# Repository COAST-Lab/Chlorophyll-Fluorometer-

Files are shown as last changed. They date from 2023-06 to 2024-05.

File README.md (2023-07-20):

# Low-Cost Chlorophyll Fluorometer 

This GitHub repository is intendied to serve as information and a guide to a low-cost chlorophyll flourometer. This fluorometer is based off of, *In situ Measurements of Phytoplankton Fluorescence Using Low Cost Electronics* and *Hardware Selection and Performance of Low-Cost Fluorometers* which can be found at https://doi.org/10.3390/s130607872 and https://doi.org/10.3390/s22062319 respectively.

## The Basics
This project is composed of a sensor packaged designed to induuce chlorphyll fluorescence and convert these values into readable measurments. This sensor contains a Particle Argon Microcontroller set to 2.30 firmware, an Arduino-Based Addalogger RTC with an SD card for data reading and writting, a TSL 2591 light sensor, an AW9523 GPIO Expander and LED Driver Guide and a Blue LED 430L for chlorophyll excitation. This design uses I2C comunication. 

# Sesnsor Construction and Testing 

## Assembly

### Step 1:
Stack the Argon Microcontroller on top of the RTC Addalogger. Connect the Argon Microcontroller to the 3.3V power source and Ground. 
### Step 2:
Set up I2C communication between the Argon Particle with the TSL 2591 and AW9523. Connect the SCL and SDA pins from the TSL 2591 Light Sensor and AW9523 GPIO Expander to the SCL and SDA pins on the Argon Microncontroller. Connect the TSL 2591 VIN pin to the 3.3V and GND pin to Ground. Connect the AW9523 VIN Pin to the 3.3V and the GND pin to Ground.
### Step 3:
Set up the LED with the AW9523. NOTE: LED negative side is connected to the pin and the positive to the power. The LED will connect to the 0 pin on the AW9523. 
### Step 4:
Assemnple the housing. The housing will position the LED and the AW9523 at a 90 degree angle as well as will be an opage design as to eliminate any ambient light from impacting the measurements. This design will then be enclosed in a waterproof box. Design materials and models can be found at https://github.com/COAST-Lab/Chlorophyll-Fluorometer-/tree/main/Firmware 
### Step 5:
Callibrate the Sensor to convert Lux values to readable measurements, based off of commerical fluoromter values. 
## Step 6:
Begin water testing 

# LED Testing 
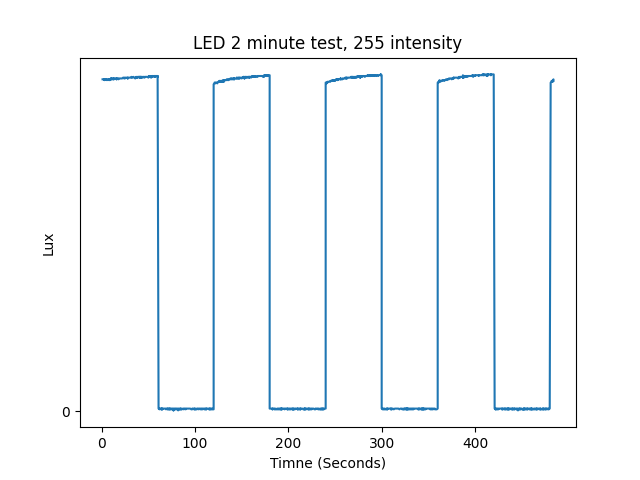
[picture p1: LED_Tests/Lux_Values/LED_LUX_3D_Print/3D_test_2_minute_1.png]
After the fluorometer was constructed, tests were run where the LED was directly facing the light sensor in a dark enviornment. This test involved turning on the LED for 2 minutes and then off for 2 minutes for 5 rounds taking light measurements throughout.  It was found that the LED was havign a steady increase in current casuing the light sensor to have an increase in values.  

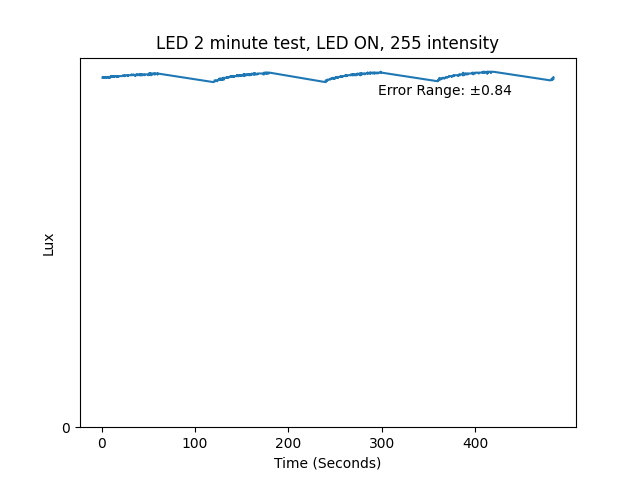
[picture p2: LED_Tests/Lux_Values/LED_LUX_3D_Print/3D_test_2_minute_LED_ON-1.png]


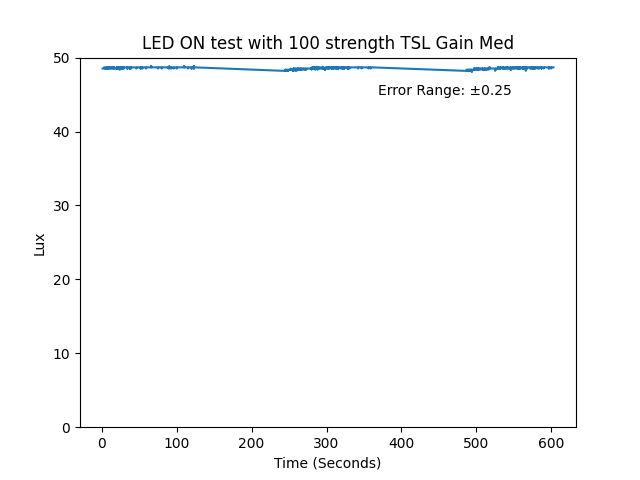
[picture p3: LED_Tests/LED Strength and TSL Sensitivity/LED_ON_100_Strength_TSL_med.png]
After many trials of this the intensity of of the LED light was changed as well as the light sensor gain (sensitivity) value. The LED can be set to any intensity from 0-255 via the AW9523. The light sesnor can be set to a gain of low, med, high and max. The LED was found to have the least variability when set to an intensity of 100 and a when the light sensor was set to a gain of med. 

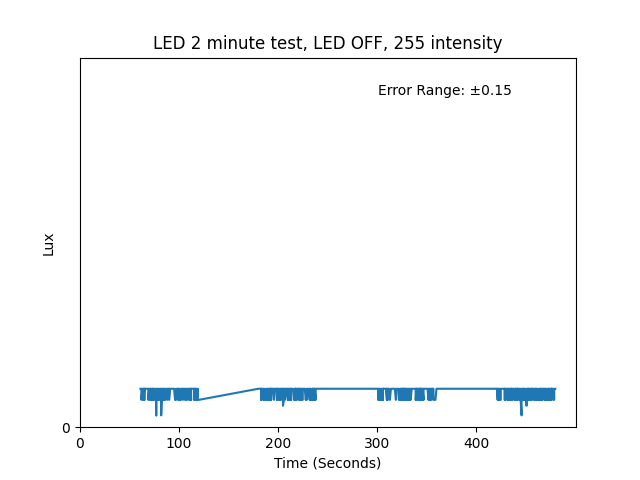
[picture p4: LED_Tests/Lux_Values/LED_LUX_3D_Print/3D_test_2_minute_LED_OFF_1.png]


After many trials of this the intensity of of the LED light was changed as well as the light sensor gain (sensitivity) value. The LED can be set to any intensity from 0-255 via the AW9523. The light sesnor can be set to a gain of low, med, high and max. The LED was found to have the least variability when set to an intensity of 100 and a when the light sensor was set to a gain of med. 

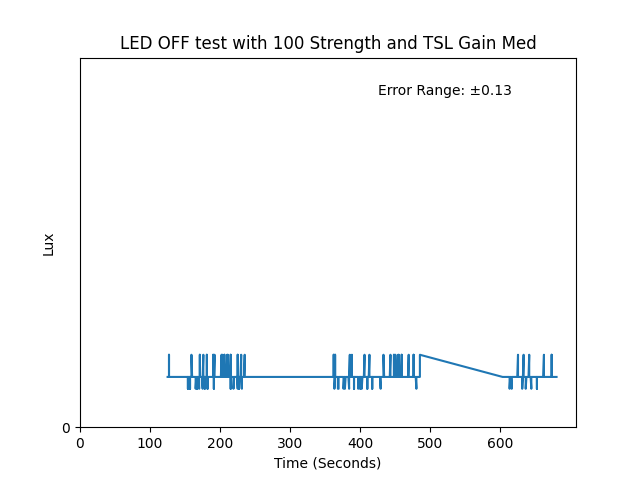
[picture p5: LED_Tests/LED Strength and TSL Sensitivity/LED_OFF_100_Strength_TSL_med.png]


```python

```

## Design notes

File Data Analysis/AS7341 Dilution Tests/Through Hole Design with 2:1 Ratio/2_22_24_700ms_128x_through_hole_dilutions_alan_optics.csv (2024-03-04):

Date and Time | ASTEP | ATIME | GAIN | LED Status | LED Intensity | Test | Seconds | Milliseconds | Type | F1 (Basic) | F2 (Basic) | F3 (Basic) | F4 (Basic) | F5 (Basic) | F6 (Basic) | F7 (Basic) | F8 (Basic) | Clear (Basic) | NIR (Basic) | Type | F1 (Raw) | F2 (Raw) | F3 (Raw) | F4 (Raw) | F5 (Raw) | F6 (Raw) | F7 (Raw) | F8 (Raw) | Clear (Raw) | NIR (Raw)
Date and Time | ASTEP | ATIME | GAIN | LED Status | LED Intensity | Test | Seconds | Milliseconds | Type | F1 (Basic) | F2 (Basic) | F3 (Basic) | F4 (Basic) | F5 (Basic) | F6 (Basic) | F7 (Basic) | F8 (Basic) | Clear (Basic) | NIR (Basic) | Type | F1 (Raw) | F2 (Raw) | F3 (Raw) | F4 (Raw) | F5 (Raw) | F6 (Raw) | F7 (Raw) | F8 (Raw) | Clear (Raw) | NIR (Raw)
2032/5/32 (Tuesday) 30:46:15 | 999 | 255 | 8 | LED ON | 255 | 0.0 | 3 | 3323 | BASIC COUNTS | 0.00 | 0.00 | 0.00 | 0.00 | 0.00 | 0.00 | 0.00 | 0.00 | 0.00 | 0.00 | RAW VALUES | 0 | 0 | 0 | 0 | 0 | 0 | 0 | 0 | 0 | 0
2032/5/32 (Tuesday) 30:46:18 | 999 | 255 | 8 | LED ON | 255 | 0.0 | 6 | 6351 | BASIC COUNTS | 0.00 | 0.01 | 0.00 | 0.00 | 0.00 | 0.00 | 0.00 | 0.00 | 0.01 | 0.00 | RAW VALUES | 398 | 637 | 57 | 29 | 20 | 23 | 29 | 18 | 620 | 0
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

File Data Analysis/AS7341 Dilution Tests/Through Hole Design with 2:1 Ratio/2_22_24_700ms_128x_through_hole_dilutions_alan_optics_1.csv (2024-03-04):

Date and Time | ASTEP | ATIME | GAIN | LED Status | LED Intensity | Test | Seconds | Milliseconds | Type | F1 (Basic) | F2 (Basic) | F3 (Basic) | F4 (Basic) | F5 (Basic) | F6 (Basic) | F7 (Basic) | F8 (Basic) | Clear (Basic) | NIR (Basic) | Type | F1 (Raw) | F2 (Raw) | F3 (Raw) | F4 (Raw) | F5 (Raw) | F6 (Raw) | F7 (Raw) | F8 (Raw) | Clear (Raw) | NIR (Raw)
2112/5/32 (Thursday) 30:46:21 | 999 | 255 | 8 | LED ON | 255 | 0.0 | 3 | 3356 | BASIC COUNTS | 0.00 | 0.00 | 0.00 | 0.00 | 0.00 | 0.00 | 0.00 | 0.00 | 0.00 | 0.00 | RAW VALUES | 0 | 0 | 0 | 0 | 0 | 0 | 0 | 0 | 0 | 0
2112/5/32 (Thursday) 30:46:24 | 999 | 255 | 8 | LED ON | 255 | 0.0 | 6 | 6383 | BASIC COUNTS | 0.00 | 0.01 | 0.00 | 0.00 | 0.00 | 0.00 | 0.00 | 0.00 | 0.01 | 0.00 | RAW VALUES | 368 | 576 | 51 | 26 | 18 | 21 | 26 | 17 | 571 | 0
2112/5/32 (Thursday) 30:46:27 | 999 | 255 | 8 | LED ON | 255 | 0.0 | 9 | 9407 | BASIC COUNTS | 0.00 | 0.01 | 0.00 | 0.00 | 0.00 | 0.00 | 0.00 | 0.00 | 0.01 | 0.00 | RAW VALUES | 367 | 577 | 51 | 26 | 19 | 21 | 26 | 17 | 570 | 0
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

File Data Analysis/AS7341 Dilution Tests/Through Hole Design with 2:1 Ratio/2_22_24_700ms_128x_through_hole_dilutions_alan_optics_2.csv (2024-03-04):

Date and Time | ASTEP | ATIME | GAIN | LED Status | LED Intensity | Test | Seconds | Milliseconds | Type | F1 (Basic) | F2 (Basic) | F3 (Basic) | F4 (Basic) | F5 (Basic) | F6 (Basic) | F7 (Basic) | F8 (Basic) | Clear (Basic) | NIR (Basic) | Type | F1 (Raw) | F2 (Raw) | F3 (Raw) | F4 (Raw) | F5 (Raw) | F6 (Raw) | F7 (Raw) | F8 (Raw) | Clear (Raw) | NIR (Raw)
2112/5/32 (Thursday) 30:46:22 | 999 | 255 | 8 | LED ON | 255 | 0.0 | 3 | 3352 | BASIC COUNTS | 0.00 | 0.00 | 0.00 | 0.00 | 0.00 | 0.00 | 0.00 | 0.00 | 0.00 | 0.00 | RAW VALUES | 0 | 0 | 0 | 0 | 0 | 0 | 0 | 0 | 0 | 0
2112/5/32 (Thursday) 30:46:25 | 999 | 255 | 8 | LED ON | 255 | 0.0 | 6 | 6380 | BASIC COUNTS | 0.00 | 0.01 | 0.00 | 0.00 | 0.00 | 0.00 | 0.00 | 0.00 | 0.01 | 0.00 | RAW VALUES | 434 | 701 | 63 | 31 | 22 | 26 | 30 | 21 | 670 | 0
2112/5/32 (Thursday) 30:46:28 | 999 | 255 | 8 | LED ON | 255 | 0.0 | 9 | 9403 | BASIC COUNTS | 0.00 | 0.01 | 0.00 | 0.00 | 0.00 | 0.00 | 0.00 | 0.00 | 0.01 | 0.00 | RAW VALUES | 432 | 702 | 63 | 31 | 22 | 26 | 31 | 21 | 671 | 0
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

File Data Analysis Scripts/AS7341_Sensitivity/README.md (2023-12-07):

# AS7341_Sensitivity

A Particle project named AS7341_Sensitivity

## Welcome to your project!

Every new Particle project is composed of 3 important elements that you'll see have been created in your project directory for AS7341_Sensitivity.

#### ```/src``` folder:  
This is the source folder that contains the firmware files for your project. It should *not* be renamed. 
Anything that is in this folder when you compile your project will be sent to our compile service and compiled into a firmware binary for the Particle device that you have targeted.

If your application contains multiple files, they should all be included in the `src` folder. If your firmware depends on Particle libraries, those dependencies are specified in the `project.properties` file referenced below.

#### ```.ino``` file:
This file is the firmware that will run as the primary application on your Particle device. It contains a `setup()` and `loop()` function, and can be written in Wiring or C/C++. For more information about using the Particle firmware API to create firmware for your Particle device, refer to the [Firmware Reference](https://docs.particle.io/reference/firmware/) section of the Particle documentation.

#### ```project.properties``` file:  
This is the file that specifies the name and version number of the libraries that your project depends on. Dependencies are added automatically to your `project.properties` file when you add a library to a project using the `particle library add` command in the CLI or add a library in the Desktop IDE.

## Adding additional files to your project

#### Projects with multiple sources
If you would like add additional files to your application, they should be added to the `/src` folder. All files in the `/src` folder will be sent to the Particle Cloud to produce a compiled binary.

#### Projects with external libraries
If your project includes a library that has not been registered in the Particle libraries system, you should create a new folder named `/lib/<libraryname>/src` under `/<project dir>` and add the `.h`, `.cpp` & `library.properties` files for your library there. Read the [Firmware Libraries guide](https://docs.particle.io/guide/tools-and-features/libraries/) for more details on how to develop libraries. Note that all contents of the `/lib` folder and subfolders will also be sent to the Cloud for compilation.

## Compiling your project

When you're ready to compile your project, make sure you have the correct Particle device target selected and run `particle compile <platform>` in the CLI or click the Compile button in the Desktop IDE. The following files in your project folder will be sent to the compile service:

- Everything in the `/src` folder, including your `.ino` application file
- The `project.properties` file for your project
- Any libraries stored under `lib/<libraryname>/src`

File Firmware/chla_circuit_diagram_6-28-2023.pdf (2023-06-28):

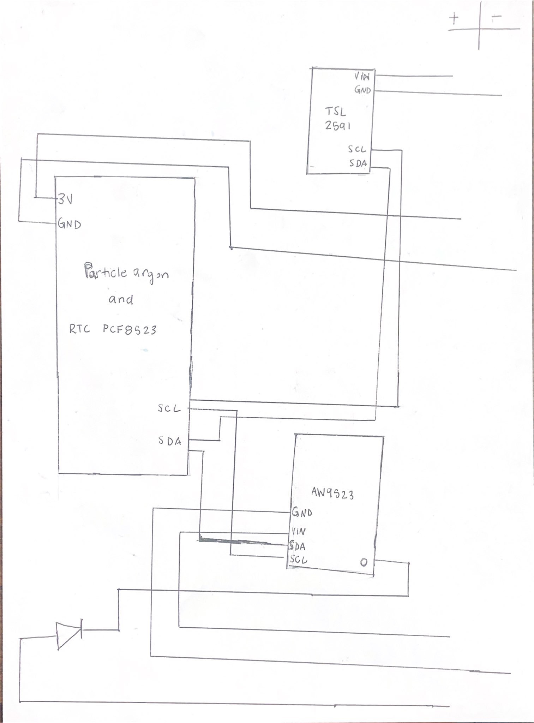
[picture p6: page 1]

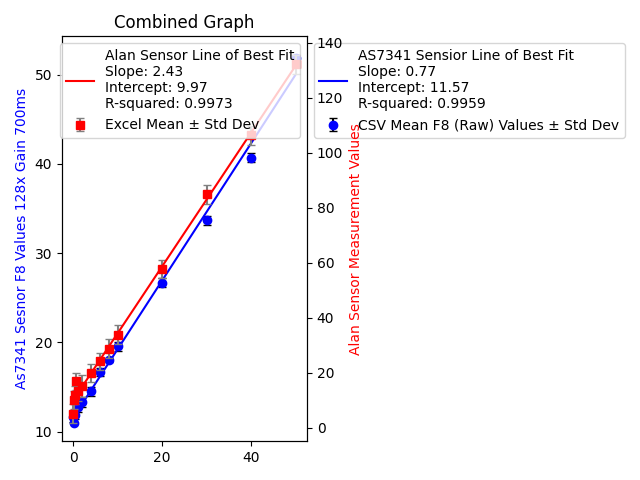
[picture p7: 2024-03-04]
Data Analysis/AS7341 Dilution Tests/Through Hole Design with 2:1 Ratio/LED with marine grade epoxy/Combined_graph_128x_700ms.png

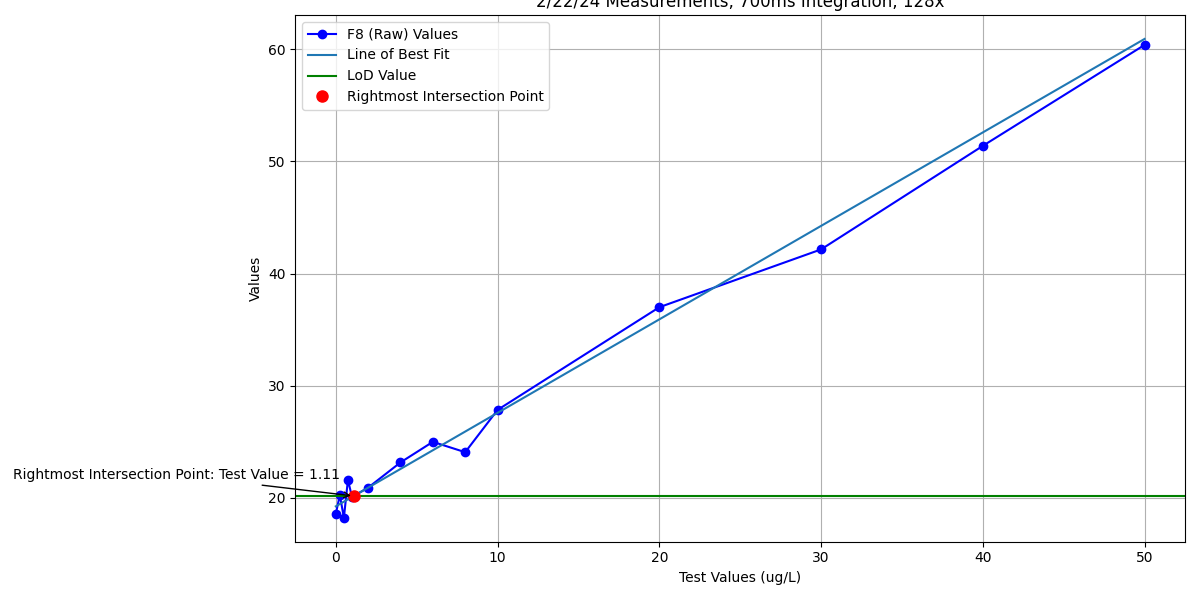
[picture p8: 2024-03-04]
Data Analysis/AS7341 Dilution Tests/Through Hole Design with 2:1 Ratio/2_22_24_128x_LoD.png

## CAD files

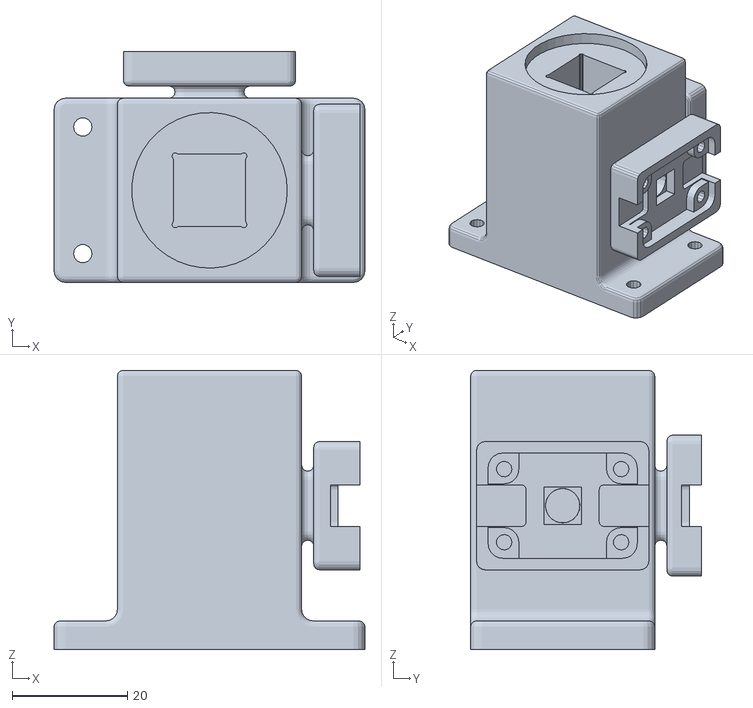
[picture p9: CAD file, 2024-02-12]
Hardware/Cuvette Holder Updated Optics/cuvette_2mm_v1r1._though_hole_1.stl
54.0 x 40.1 x 48.5

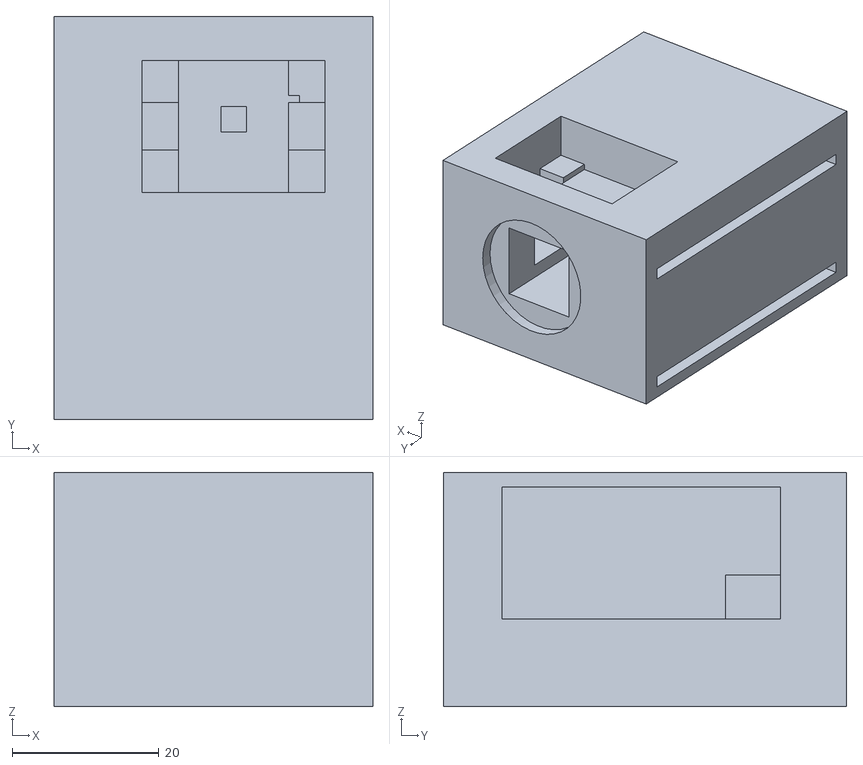
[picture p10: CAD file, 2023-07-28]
Hardware/Cuvette Holder/cuvette holder v3.stl
43.5 x 55.0 x 32.0

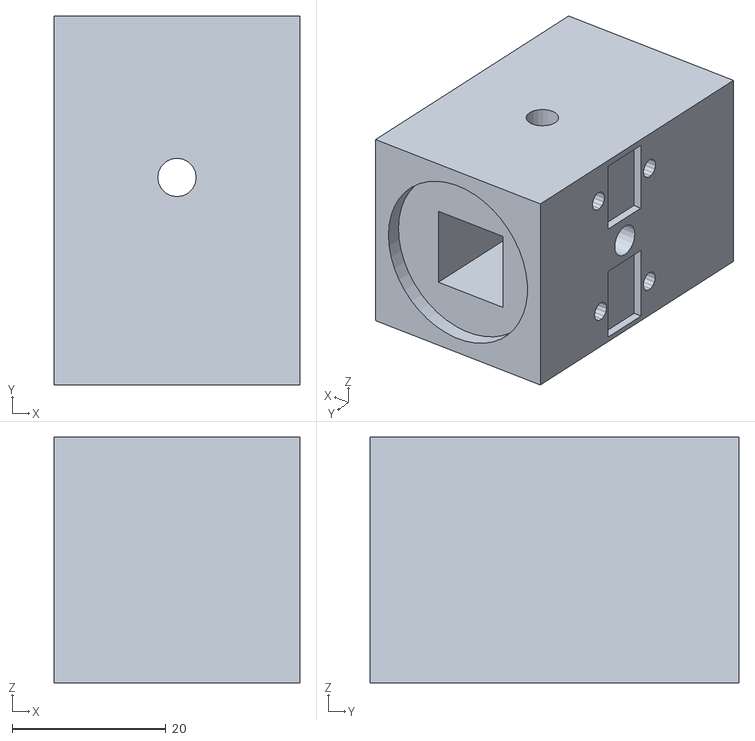
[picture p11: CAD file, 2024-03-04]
Hardware/Cuvette Holder/Through Hole Designs/2_1_through_hole_ratio.stl
32.0 x 48.0 x 32.0

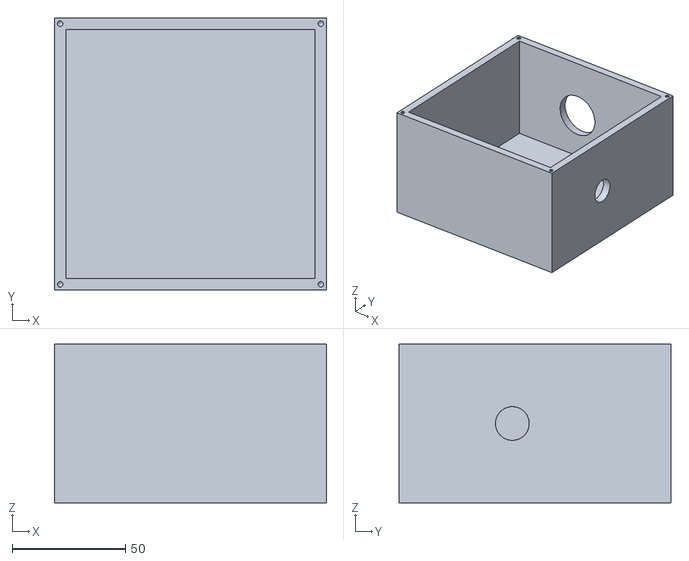
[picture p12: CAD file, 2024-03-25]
Hardware/Housing/3D_Housing_2_19_24/3d_enclosure_2_19_1.stl
120.0 x 120.0 x 70.0

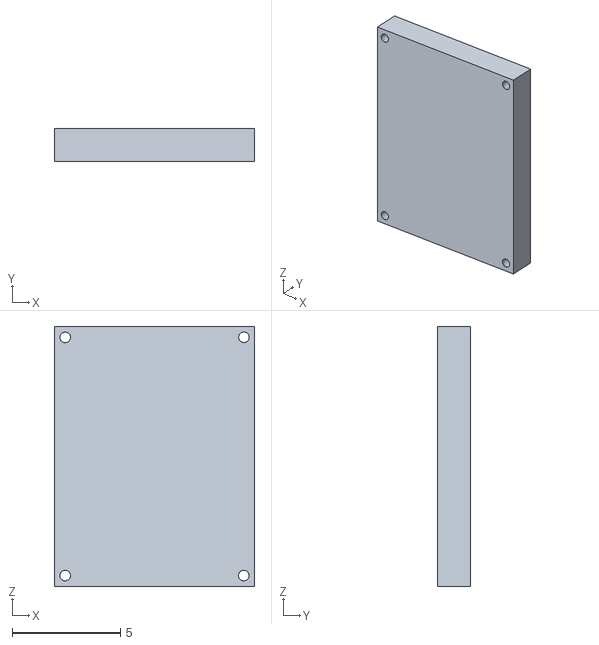
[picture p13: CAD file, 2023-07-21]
Hardware/Housing/Water_Proof_Box_Top_2.stl
9.25 x 1.50 x 12.0

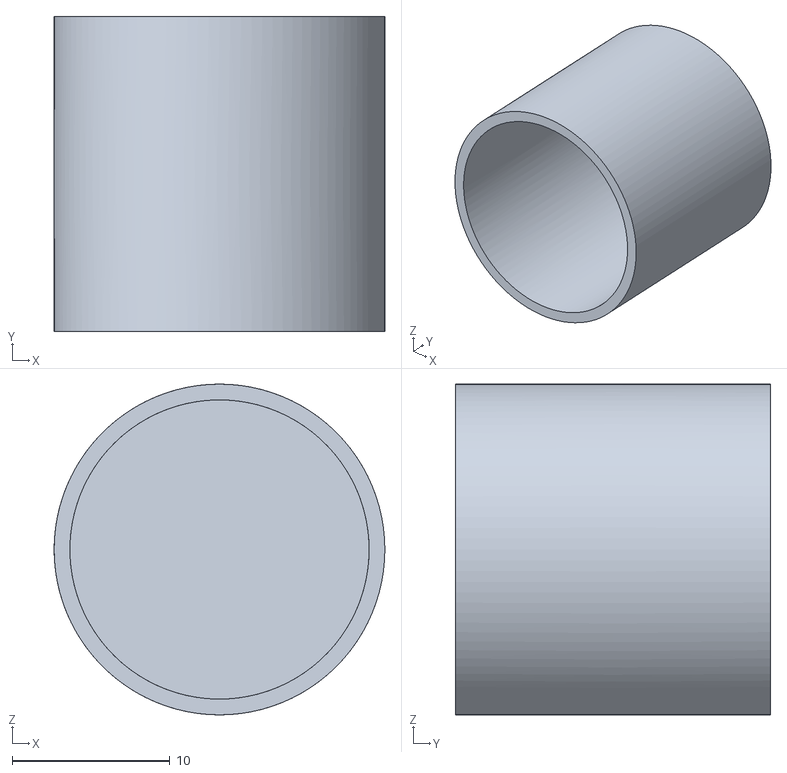
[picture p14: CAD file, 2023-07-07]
Hardware/Light Blocking Cap/Light_Blocking_Cap.stl
21.0 x 20.0 x 21.0

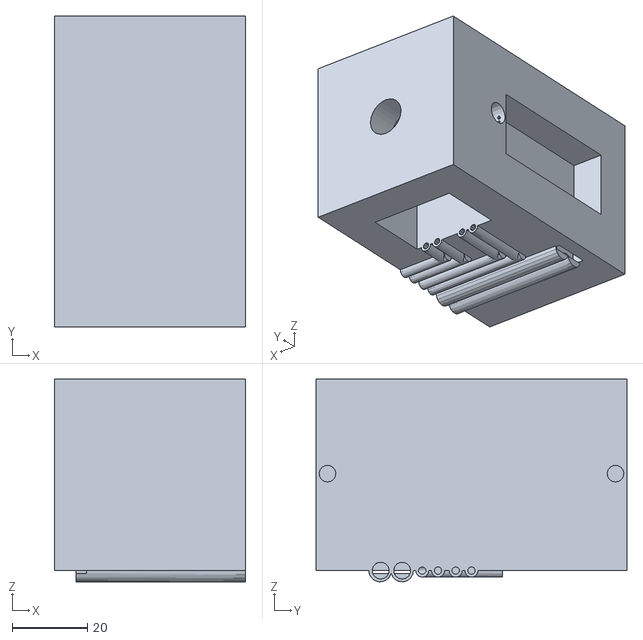
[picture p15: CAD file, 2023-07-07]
Hardware/Cuvette Holder/Cuvette holder v1.stl
50.8 x 82.6 x 53.8

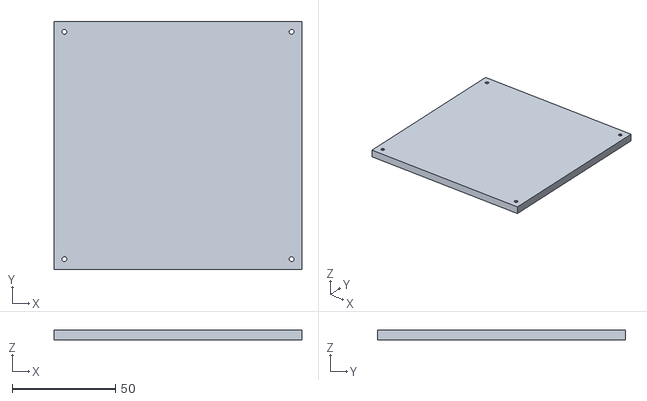
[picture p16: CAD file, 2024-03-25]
Hardware/Housing/3D_Housing_2_19_24/3d_enclosure_2_19_top_1.stl
120.0 x 120.0 x 5.00

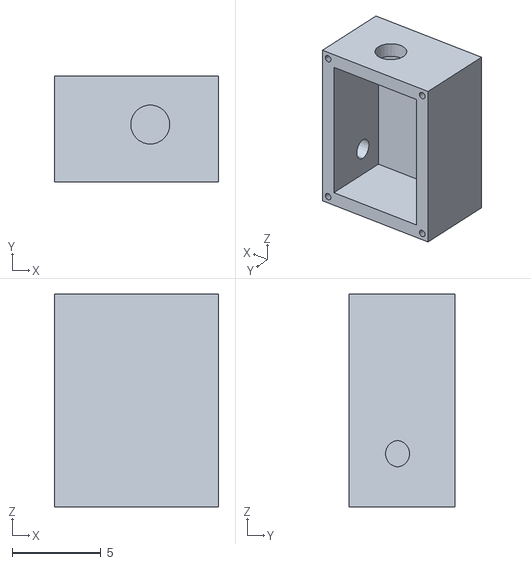
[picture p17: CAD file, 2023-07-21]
Hardware/Housing/Water_Proof_Box_Bottom.stl
9.25 x 6.00 x 12.0

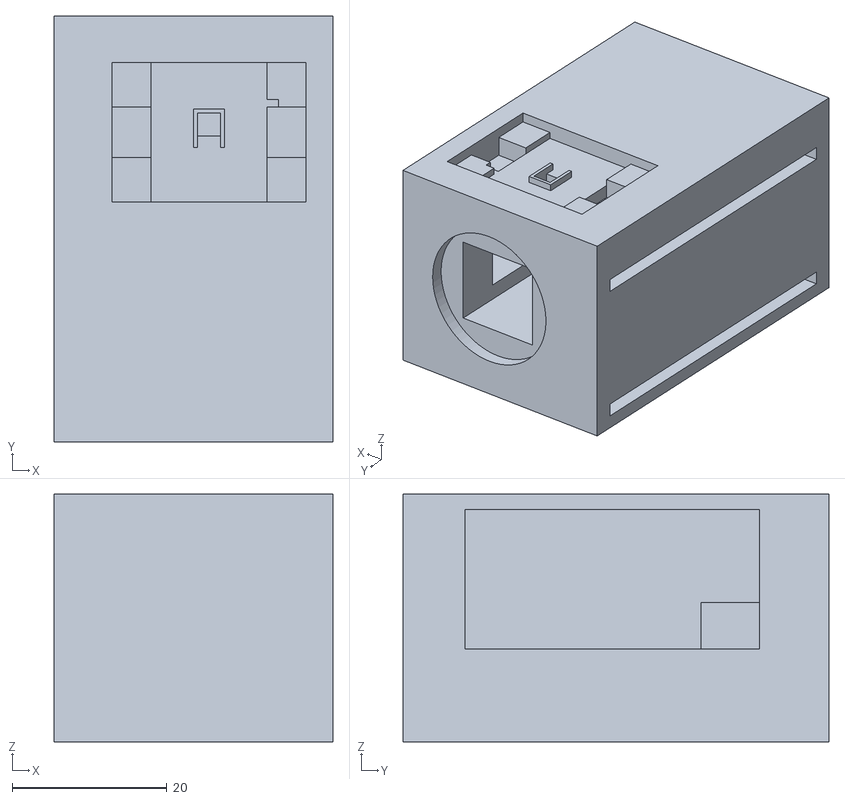
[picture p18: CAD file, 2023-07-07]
Hardware/Cuvette Holder/Cuvette Holder v2.stl
36.0 x 55.0 x 32.0

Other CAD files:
Hardware/Cuvette Holder Updated Optics/cuvett_holder_updated_optics_2.stl
Hardware/Cuvette Holder Updated Optics/cuvett_holder_updated_optics.stl
Hardware/Cuvette Holder Updated Optics/cuvett_holder_updated_optics.ipt
Hardware/Cuvette Holder Updated Optics/cuvett_holder_updated_optics_2.ipt
Hardware/Cuvette Holder Updated Optics/cuvette_2mm_v1r1._though_hole_1.ipt
Hardware/Cuvette Holder/Cuvette Holder v2.ipt
Hardware/Cuvette Holder/Through Hole Designs/2_1_through_hole_ratio.ipt
Hardware/Cuvette Holder/cuvette holder v1.ipt
Hardware/Cuvette Holder/cuvette holder v3.ipt
Hardware/Housing/3D_Housing_2_19_24/3d_enclosure_2_19_1.ipt
Hardware/Housing/3D_Housing_2_19_24/3d_enclosure_2_19_top_1.ipt
Hardware/Housing/Water_Proof_Box_Bottom.ipt
Hardware/Housing/Water_Proof_Box_Top_2.ipt
Hardware/Light Blocking Cap/Light_Blocking_Cap.ipt

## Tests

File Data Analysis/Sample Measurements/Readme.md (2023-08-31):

## Description
This is the analysis of the chlorophyll fluorometer by taking measurements 
of chlorophyll standards via rhodamine dye. These tests serve as an analysis
of the fluorometer's functionality for future testing. 

# Fluormeter Testing

## Fluormeter Design 
This fluorometer is a benchtop model with housing which positions the LED and 
the TSL2592 at a 90-degree angle as well as will be an opaque design as to 
eliminate any ambient light from impacting the measurements. The TSL 2591
is fitted with a red filter Rocsculux filter #19. This filter had a 20% transmission.
The top of the benchtop design contains a hole 
that fits a cuvette. A cuvette is placed into the fluorometer with the water
sample to begin testing. Design materials can be found at:
https://github.com/COAST-Lab/Chlorophyll-Fluorometer-/tree/main/Firmware. 

Device diagram

## Testing Procedure 

### Step 1
A YSI instrument was calibrated to be used to verify the chlorophyll water sample
which would be prepared. Calibration information: 
https://www.ysi.com/file%20library/documents/manuals/exo-user-manual-web.pdf

### Step 2
A water sample was prepared with a chlorophyll concentration of 63.5 ug/L and 
an RFU of 15.8 RFU. This water sample was prepared with rhodamine dye and DI water

#### Chlorophyll Sample Preparation
###### Step 1
5mL of Rhodamine dye was pipetted into a 1000mL volumetric flask or beaker. Fill 
the flask or beaker up to 1000mL mark with DI water
    
###### Step 2
Pipette 5mL of the prepared solution in step 1 into a separate 1000mL volumetric
flask or beaker. Fill this flask or beaker up to 1000mL mark with DI water. This
will be your chlorophyll water sample

###### Step 3
Verify the concentration of the prepared chlorophyll water sample with the YSI

### Step 3
Insert an empty cuvette into the fluorometer housing. Cover the fluorometer with a 
cardboard box to ensure it is in complete darkness. Modify the code to turn the LED OFF
and run for 1 minute 



### Step 4
Repeat step 3 with the LED ON 

### Step 5
Stop readings and take the empty cuvette out of the fluorometer. Insert a cuvette 
filled with DI water into the fluorometer. Recover with the box and run the code 
with the LED ON for one minute

### Step 6
Stop readings and take the cuvette filled with DI water out of the flurometer. 
Insert a cuvette filled with chlorophyll water solution into the fluorometer. 
Recover with the box and run the code with the LED ON for one minute

### Step 7
Stop testing and take the SD card out of the fluorometer and plug it into the 
computer to begin analysis of the data collected. 

### Step 8
This test will be performed first with an LED intensity of 250 and a TSL 2591
gain of HIGH and then repeated with a LED intensity of 255 and a TSL 2591
gain of MAX. 

## Data Analysis 

### Graphing 
When taking measurements the TSL 2591 light sensor collects light measurements 
of Visible, Full, IR, and Lux. Data analysis will be performed on Visible, Full
, and Lux. 

#### Graph characteristics
Each graph shows the catagories of 'cuvette dark', 'cuvette light', 'DI Water' 
and '63.5 ug/L' on the x-axis to denote each test. And the numerical value of 
the light measurement on the y-axis. The mean of each category will be plotted
with an error bar with extends from the lowest value of the data set to 
the largest. 

## Lux Graphs 

Chlorophyll_Sample_Tests_LED_250_Gain_High_Lux

Chlorophyll_Sample_Tests_LED_255_Gain_Max_Lux

## Visible Graphs 

Chlorophyll_Sample_Tests_LED_250_Gain_High_Visible

Chlorophyll_Sample_Tests_LED_255_Gain_Max_Visible

## Full Graphs 
Chlorophyll_Sample_Tests_LED_250_Gain_High_Full

Chlorophyll_Sample_Tests_LED_255_Gain_Max_Full

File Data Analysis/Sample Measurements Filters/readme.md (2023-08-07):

# Description
This is the analysis of the chlorophyll fluorometer by taking measurements 
of chlorophyll standards via rhodamine dye. This analysis is to test the use
of filters with different transmissions to evaluate if higher transmissions lead 
to less overlap in measurements. 

# Fluormeter Testing

## Fluormeter Design 
This fluorometer is a benchtop model with housing which positions the LED and 
the TSL2592 at a 90-degree angle as well as will be an opaque design as to 
eliminate any ambient light from impacting the measurements. The TSL 2591
has been fitted with either a Rosculox #18 filter (56% transmission) or a Rosculox
#321 filter (39% transmission). The top of the benchtop design contains a hole 
that fits a cuvette. To begin testing, a cuvette is placed into the fluorometer with the water
sample. Design materials can be found at:
https://github.com/COAST-Lab/Chlorophyll-Fluorometer-/tree/main/Firmware. 

Device diagram

## Filters
Filters fitted over the light sensor are used to commit the blue excitation light from
being measured. Red filters with wavelengths between 690-740nm are usually used
to accomplish this. The filter used in this test, Rsoculox filters #18 and #321 have 
wavelengths of approximately 620-700nm and 660-700nm respectively. 




## Testing Procedure 

### Step 1
A YSI instrument was calibrated to be used to verify the chlorophyll water sample
which would be prepared. Calibration information: 
https://www.ysi.com/file%20library/documents/manuals/exo-user-manual-web.pdf

### Step 2
A water sample was prepared with a chlorophyll concentration of 6.5mg/L and 
an RFU of 15.8 RFU. This water sample was prepared with rhodamine dye and DI water

#### Chlorophyll Sample Preparation
###### Step 1
5mL of Rhodamine dye was pipetted into a 1000mL volumetric flask or beaker. Fill 
the flask or beaker up to 1000mL mark with DI water
    
###### Step 2
Pipette 5mL of the prepared solution in step 1 into a separate 1000mL volumetric
flask or beaker. Fill this flask or beaker up to 1000mL mark with DI water. This
will be your chlorophyll water sample

###### Step 3
Verify the concentration of the prepared chlorophyll water sample with the YSI

### Step 3
Insert an empty cuvette into the fluorometer housing. Cover the fluorometer with a 
cardboard box to ensure it is in complete darkness. Modify the code to turn the LED OFF
and run for 1 minute 



### Step 4
Repeat step 3 with the LED ON 

### Step 5
Stop readings and take the empty cuvette out of the fluorometer. Insert a cuvette 
filled with DI water into the fluorometer. Recover with the box and run the code 
with the LED ON for one minute

### Step 6
Stop readings and take the cuvette filled with DI water out of the fluorometer. 
Insert a cuvette filled with chlorophyll water solution into the fluorometer. 
Recover with the box and run the code with the LED ON for one minute

### Step 7
Stop testing and take the SD card out of the fluorometer and plug it into the 
computer to begin analysis of the data collected. 

### Step 8
This test will be performed first with an LED intensity of 250 and a TSL 2591
gain of HIGH and then repeated with a LED intensity of 255 and a TSL 2591
gain of MAX. 

This test was completed once with the Rosculox #18 filter and then again
with the #321 filter. 

## Data Analysis 

### Graphing 
When taking measurements the TSL 2591 light sensor collects light measurements 
of Visible, Full, IR, and Lux. Data analysis will be performed on Visible, Full
, and Lux. 

#### Graph characteristics
Each graph shows the catagories of 'cuvette dark', 'cuvette light', 'DI Water' 
and '6.5 mg/L' on the x-axis to denote each test. And the numerical value of 
the light measurement on the y-axis. The mean of each category will be plotted
with an error bar with extends from the lowest value of the data set to 
the largest. 

## Lux Graph #18 Filter

chl_sample_filter_18_lux

## Lux Graph #321 Filter

chl_sample_filter_321

## Visible Graph #18 Filter
chl_sample_filter_18_visible

## Visible Graph #321 Filter
chl_sample_filter_321_visible

## Full Graph #18 Filter
chl_sample_filter_18_full

## Full Graph #321 Filter 
chl_sample_filter_321_full

# Conclusion
It seems that the greater the transmission of the filter, the higher the light measurements
are. This could be beneficial as the LED is able to penetrate through these filters more
and possibly lead to higher sensitivity when measuring chlorophyll fluorescence. 

```python

```

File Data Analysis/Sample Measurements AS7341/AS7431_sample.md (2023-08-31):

# Description
This is the analysis of the chlorophyll fluorometer by taking measurements of chlorophyll standards via rhodamine dye. These tests serve as an analysis of the fluorometer's functionality for future testing.

# Fluormeter Testing

## Fluormeter Design
This fluorometer is a benchtop model with housing which positions the LED and the AS7341 at a 90-degree angle as well as will be an opaque design as to eliminate any ambient light from impacting the measurements. The AS7341 is fitted with a red filter Rocsculux filter #19. This filter had a 20% transmission. The top of the benchtop design contains a hole that fits a cuvette. A cuvette is placed into the fluorometer with the water sample to begin testing. Design materials can be found at: https://github.com/COAST-Lab/Chlorophyll-Fluorometer-/tree/main/Firmware.

# Testing Procedure

## Step 1
A YSI instrument was calibrated to be used to verify the chlorophyll water sample which would be prepared. Calibration information: https://www.ysi.com/file%20library/documents/manuals/exo-user-manual-web.pdf

## Step 2
A water sample was prepared with a chlorophyll concentration of 6.5mg/L and an RFU of 15.8 RFU. This water sample was prepared with rhodamine dye and DI water

## Chlorophyll Sample Preparation
### Step 1
5mL of Rhodamine dye was pipetted into a 1000mL volumetric flask or beaker. Fill the flask or beaker up to 1000mL mark with DI water

### Step 2
Pipette 5mL of the prepared solution in step 1 into a separate 1000mL volumetric flask or beaker. Fill this flask or beaker up to 1000mL mark with DI water. This will be your chlorophyll water sample

### Step 3
Verify the concentration of the prepared chlorophyll water sample with the YSI

## Step 3
Insert an empty cuvette into the fluorometer housing. Cover the fluorometer with a cardboard box to ensure it is in complete darkness. Modify the code to turn the LED OFF and run for 1 minute

## Step 4
Repeat step 3 with the LED ON

## Step 5
Stop readings and take the empty cuvette out of the fluorometer. Insert a cuvette filled with DI water into the fluorometer. Recover with the box and run the code with the LED ON for one minute

## Step 6
Stop readings and take the cuvette filled with DI water out of the flurometer. Insert a cuvette filled with chlorophyll water solution into the fluorometer. Recover with the box and run the code with the LED ON for one minute

## Step 7
Stop testing and take the SD card out of the fluorometer and plug it into the computer to begin analysis of the data collected.

## Step 8
This test will be performed first with an LED intensity of 255 and an AS73411 gain of 512x and an ATIME of 59 and ASTEP of 599 and then repeated with a gain of 64x and then 4x. The data is recorded onto the SD card in the microcontroller. 

# Data Analysis

## Graphing
When taking measurements the AS7341 light sensor collects light measurements of multiple wavelengths. The wavelength of 680nm (denoted as F8) will be analyzed.

## Graph characteristics
Each graph shows the categories of 'cuvette dark', 'cuvette light', 'DI Water Dark', 'DI Water Light' and '6.5 mg/L' on the x-axis to denote each test. And the numerical value of the F8 light measurement on the y-axis. The mean of each category will be plotted with an error bar with extends from the lowest value of the data set to the largest.

## 512x Gain Graph
chl_sample_AS7341_512

## 64x Gain Graph
chl_sample_AS7431_64

## 4x Gain Graph
chl_sample_AS7341_4

```python

```

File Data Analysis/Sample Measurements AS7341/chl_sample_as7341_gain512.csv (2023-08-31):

Date and Time | LED Status | LED Intensity | Test | Milliseconds | Seconds | Type | F1 (Basic) | F2 (Basic) | F3 (Basic) | F4 (Basic) | F5 (Basic) | F6 (Basic) | F7 (Basic) | F8 (Basic) | Clear (Basic) | NIR (Basic) | Type | F1 (Raw) | F2 (Raw) | F3 (Raw) | F4 (Raw) | F5 (Raw) | F6 (Raw) | F7 (Raw) | F8 (Raw) | Clear (Raw) | NIR (Raw)
2023/8/7 (Monday) 11:58:29 | LED OFF | 0 | Cuvette Dark | 0 | 975 | BASIC COUNTS | 0.00 | 0.00 | 0.00 | 0.00 | 0.00 | 0.00 | 0.00 | 0.00 | 0.00 | 0.00 | RAW VALUES | 0 | 0 | 0 | 0 | 0 | 0 | 0 | 0 | 0 | 0
2023/8/7 (Monday) 11:58:30 | LED OFF | 0 | Cuvette Dark | 1 | 1639 | BASIC COUNTS | 0.00 | 0.00 | 0.00 | 0.00 | 0.00 | 0.00 | 0.00 | 0.00 | 0.00 | 0.00 | RAW VALUES | 0 | 0 | 0 | 0 | 0 | 0 | 0 | 0 | 0 | 0
2023/8/7 (Monday) 11:58:30 | LED OFF | 0 | Cuvette Dark | 2 | 2303 | BASIC COUNTS | 0.00 | 0.00 | 0.00 | 0.00 | 0.00 | 0.00 | 0.00 | 0.00 | 0.00 | 0.00 | RAW VALUES | 0 | 0 | 0 | 0 | 0 | 0 | 0 | 0 | 0 | 0
2023/8/7 (Monday) 11:58:31 | LED OFF | 0 | Cuvette Dark | 2 | 2965 | BASIC COUNTS | 0.00 | 0.00 | 0.00 | 0.00 | 0.00 | 0.00 | 0.00 | 0.00 | 0.00 | 0.00 | RAW VALUES | 0 | 0 | 0 | 0 | 0 | 0 | 0 | 0 | 0 | 0
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

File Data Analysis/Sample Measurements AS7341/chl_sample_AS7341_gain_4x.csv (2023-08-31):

Date and Time | ASTEP | ATIME | GAIN | LED Status | LED Intensity | Test | Milliseconds | Seconds | Type | F1 (Basic) | F2 (Basic) | F3 (Basic) | F4 (Basic) | F5 (Basic) | F6 (Basic) | F7 (Basic) | F8 (Basic) | Clear (Basic) | NIR (Basic) | Type | F1 (Raw) | F2 (Raw) | F3 (Raw) | F4 (Raw) | F5 (Raw) | F6 (Raw) | F7 (Raw) | F8 (Raw) | Clear (Raw) | NIR (Raw)
Date and Time | ASTEP | ATIME | GAIN | LED Status | LED Intensity | Test | Milliseconds | Seconds | Type | F1 (Basic) | F2 (Basic) | F3 (Basic) | F4 (Basic) | F5 (Basic) | F6 (Basic) | F7 (Basic) | F8 (Basic) | Clear (Basic) | NIR (Basic) | Type | F1 (Raw) | F2 (Raw) | F3 (Raw) | F4 (Raw) | F5 (Raw) | F6 (Raw) | F7 (Raw) | F8 (Raw) | Clear (Raw) | NIR (Raw)
2023/8/7 (Monday) 13:5:35 | 599 | 59 | 3 | LED OFF | 0 | Cuvette Dark | 0 | 971 | BASIC COUNTS | 0.00 | 0.00 | 0.00 | 0.00 | 0.00 | 0.00 | 0.00 | 0.00 | 0.00 | 0.00 | RAW VALUES | 0 | 0 | 0 | 0 | 0 | 0 | 0 | 0 | 0 | 0
2023/8/7 (Monday) 13:5:35 | 599 | 59 | 3 | LED OFF | 0 | Cuvette Dark | 1 | 1632 | BASIC COUNTS | 0.00 | 0.00 | 0.00 | 0.00 | 0.00 | 0.00 | 0.00 | 0.00 | 0.00 | 0.00 | RAW VALUES | 0 | 0 | 0 | 0 | 0 | 0 | 0 | 0 | 0 | 0
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

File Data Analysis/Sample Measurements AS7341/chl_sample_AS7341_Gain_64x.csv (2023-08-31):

Date and Time | ASTEP | ATIME | GAIN | LED Status | LED Intensity | Test | Milliseconds | Seconds | Type | F1 (Basic) | F2 (Basic) | F3 (Basic) | F4 (Basic) | F5 (Basic) | F6 (Basic) | F7 (Basic) | F8 (Basic) | Clear (Basic) | NIR (Basic) | Type | F1 (Raw) | F2 (Raw) | F3 (Raw) | F4 (Raw) | F5 (Raw) | F6 (Raw) | F7 (Raw) | F8 (Raw) | Clear (Raw) | NIR (Raw)
2023/8/7 (Monday) 13:27:35 | 599 | 59 | 7 | LED OFF | 0 | Cuvette Dark | 0 | 972 | BASIC COUNTS | 0.00 | 0.00 | 0.00 | 0.00 | 0.00 | 0.00 | 0.00 | 0.00 | 0.00 | 0.00 | RAW VALUES | 0 | 0 | 0 | 0 | 0 | 0 | 0 | 0 | 0 | 0
2023/8/7 (Monday) 13:27:36 | 599 | 59 | 7 | LED OFF | 0 | Cuvette Dark | 1 | 1635 | BASIC COUNTS | 0.00 | 0.00 | 0.00 | 0.00 | 0.00 | 0.00 | 0.00 | 0.00 | 0.00 | 0.00 | RAW VALUES | 0 | 0 | 0 | 0 | 0 | 0 | 0 | 0 | 0 | 0
2023/8/7 (Monday) 13:27:36 | 599 | 59 | 7 | LED OFF | 0 | Cuvette Dark | 2 | 2297 | BASIC COUNTS | 0.00 | 0.00 | 0.00 | 0.00 | 0.00 | 0.00 | 0.00 | 0.00 | 0.00 | 0.00 | RAW VALUES | 0 | 0 | 0 | 0 | 0 | 0 | 0 | 0 | 0 | 0
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

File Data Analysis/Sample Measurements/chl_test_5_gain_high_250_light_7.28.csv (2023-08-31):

Time | Seconds | Milliseconds | IR | Full | Visible | Lux | LED Status | LED Intensity | Test
2023/7/25 (Tuesday) 16:18:51 | 1 | 1266 | 1 | 1 | 0 | 0.00 | LED OFF | 0 | cuvette dark
2023/7/25 (Tuesday) 16:18:51 | 1 | 1568 | 1 | 1 | 0 | 0.00 | LED OFF | 0 | cuvette dark
2023/7/25 (Tuesday) 16:18:51 | 1 | 1871 | 1 | 1 | 0 | 0.00 | LED OFF | 0 | cuvette dark
2023/7/25 (Tuesday) 16:18:51 | 2 | 2173 | 0 | 1 | 1 | 0.16 | LED OFF | 0 | cuvette dark
2023/7/25 (Tuesday) 16:18:51 | 2 | 2475 | 0 | 1 | 1 | 0.16 | LED OFF | 0 | cuvette dark
2023/7/25 (Tuesday) 16:18:51 | 2 | 2779 | 1 | 1 | 0 | 0.00 | LED OFF | 0 | cuvette dark
2023/7/25 (Tuesday) 16:18:51 | 3 | 3081 | 1 | 1 | 0 | 0.00 | LED OFF | 0 | cuvette dark
2023/7/25 (Tuesday) 16:18:51 | 3 | 3383 | 1 | 1 | 0 | 0.00 | LED OFF | 0 | cuvette dark
2023/7/25 (Tuesday) 16:18:51 | 3 | 3685 | 1 | 1 | 0 | 0.00 | LED OFF | 0 | cuvette dark
2023/7/25 (Tuesday) 16:18:51 | 3 | 3988 | 1 | 1 | 0 | 0.00 | LED OFF | 0 | cuvette dark
2023/7/25 (Tuesday) 16:18:51 | 4 | 4291 | 1 | 1 | 0 | 0.00 | LED OFF | 0 | cuvette dark
2023/7/25 (Tuesday) 16:18:51 | 4 | 4593 | 1 | 1 | 0 | 0.00 | LED OFF | 0 | cuvette dark
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

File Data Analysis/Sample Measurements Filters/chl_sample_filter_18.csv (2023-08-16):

Time | Seconds | Milliseconds | IR | Full | Visible | Lux | LED Status | LED Intensity | Test
2023/7/30 (Sunday) 12:32:0 | 1 | 1266 | 2 | 7 | 5 | 0.58 | LED OFF | 0 | Cuvette Dark
2023/7/30 (Sunday) 12:32:0 | 1 | 1569 | 2 | 7 | 5 | 0.58 | LED OFF | 0 | Cuvette Dark
2023/7/30 (Sunday) 12:32:0 | 1 | 1871 | 2 | 7 | 5 | 0.58 | LED OFF | 0 | Cuvette Dark
2023/7/30 (Sunday) 12:32:0 | 2 | 2173 | 1 | 7 | 6 | 0.84 | LED OFF | 0 | Cuvette Dark
2023/7/30 (Sunday) 12:32:0 | 2 | 2474 | 2 | 7 | 5 | 0.58 | LED OFF | 0 | Cuvette Dark
2023/7/30 (Sunday) 12:32:0 | 2 | 2776 | 2 | 7 | 5 | 0.58 | LED OFF | 0 | Cuvette Dark
2023/7/30 (Sunday) 12:32:0 | 3 | 3078 | 2 | 7 | 5 | 0.58 | LED OFF | 0 | Cuvette Dark
2023/7/30 (Sunday) 12:32:0 | 3 | 3380 | 2 | 7 | 5 | 0.58 | LED OFF | 0 | Cuvette Dark
2023/7/30 (Sunday) 12:32:0 | 3 | 3684 | 2 | 7 | 5 | 0.58 | LED OFF | 0 | Cuvette Dark
2023/7/30 (Sunday) 12:32:0 | 3 | 3987 | 1 | 7 | 6 | 0.84 | LED OFF | 0 | Cuvette Dark
2023/7/30 (Sunday) 12:32:0 | 4 | 4289 | 1 | 7 | 6 | 0.84 | LED OFF | 0 | Cuvette Dark
2023/7/30 (Sunday) 12:32:0 | 4 | 4592 | 2 | 7 | 5 | 0.58 | LED OFF | 0 | Cuvette Dark
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

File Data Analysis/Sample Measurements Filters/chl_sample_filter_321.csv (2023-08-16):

Time | Seconds | Milliseconds | IR | Full | Visible | Lux | LED Status | LED Intensity | Test
2023/7/30 (Sunday) 12:59:32 | 1 | 1550 | 0 | 1 | 1 | 0.16 | LED OFF | 0 | Cuvette Dark
2023/7/30 (Sunday) 12:59:32 | 1 | 1852 | 0 | 1 | 1 | 0.16 | LED OFF | 0 | Cuvette Dark
2023/7/30 (Sunday) 12:59:32 | 2 | 2155 | 0 | 1 | 1 | 0.16 | LED OFF | 0 | Cuvette Dark
2023/7/30 (Sunday) 12:59:32 | 2 | 2457 | 0 | 1 | 1 | 0.16 | LED OFF | 0 | Cuvette Dark
2023/7/30 (Sunday) 12:59:32 | 2 | 2759 | 0 | 1 | 1 | 0.16 | LED OFF | 0 | Cuvette Dark
2023/7/30 (Sunday) 12:59:32 | 3 | 3062 | 0 | 1 | 1 | 0.16 | LED OFF | 0 | Cuvette Dark
2023/7/30 (Sunday) 12:59:32 | 3 | 3364 | 0 | 1 | 1 | 0.16 | LED OFF | 0 | Cuvette Dark
2023/7/30 (Sunday) 12:59:32 | 3 | 3667 | 0 | 1 | 1 | 0.16 | LED OFF | 0 | Cuvette Dark
2023/7/30 (Sunday) 12:59:32 | 3 | 3971 | 0 | 1 | 1 | 0.16 | LED OFF | 0 | Cuvette Dark
2023/7/30 (Sunday) 12:59:32 | 4 | 4274 | 0 | 1 | 1 | 0.16 | LED OFF | 0 | Cuvette Dark
2023/7/30 (Sunday) 12:59:32 | 4 | 4577 | 0 | 1 | 1 | 0.16 | LED OFF | 0 | Cuvette Dark
2023/7/30 (Sunday) 12:59:32 | 4 | 4880 | 0 | 1 | 1 | 0.16 | LED OFF | 0 | Cuvette Dark
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

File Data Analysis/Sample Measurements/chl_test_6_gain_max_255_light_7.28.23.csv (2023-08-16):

Time | Seconds | Milliseconds | IR | Full | Visible | Lux | LED Status | LED Intensity | Test
2023/7/25 (Tuesday) 16:30:2 | 1 | 1266 | 1 | 1 | 0 | 0.00 | LED OFF | 0 | cuvette dark
2023/7/25 (Tuesday) 16:30:2 | 1 | 1568 | 1 | 1 | 0 | 0.00 | LED OFF | 0 | cuvette dark
2023/7/25 (Tuesday) 16:30:2 | 1 | 1870 | 1 | 1 | 0 | 0.00 | LED OFF | 0 | cuvette dark
2023/7/25 (Tuesday) 16:30:2 | 2 | 2172 | 1 | 1 | 0 | 0.00 | LED OFF | 0 | cuvette dark
2023/7/25 (Tuesday) 16:30:2 | 2 | 2476 | 1 | 1 | 0 | 0.00 | LED OFF | 0 | cuvette dark
2023/7/25 (Tuesday) 16:30:2 | 2 | 2780 | 1 | 1 | 0 | 0.00 | LED OFF | 0 | cuvette dark
2023/7/25 (Tuesday) 16:30:2 | 3 | 3082 | 1 | 1 | 0 | 0.00 | LED OFF | 0 | cuvette dark
2023/7/25 (Tuesday) 16:30:2 | 3 | 3390 | 0 | 1 | 1 | 0.16 | LED OFF | 0 | cuvette dark
2023/7/25 (Tuesday) 16:30:2 | 3 | 3692 | 1 | 1 | 0 | 0.00 | LED OFF | 0 | cuvette dark
2023/7/25 (Tuesday) 16:30:2 | 3 | 3994 | 1 | 1 | 0 | 0.00 | LED OFF | 0 | cuvette dark
2023/7/25 (Tuesday) 16:30:2 | 4 | 4297 | 1 | 1 | 0 | 0.00 | LED OFF | 0 | cuvette dark
2023/7/25 (Tuesday) 16:30:2 | 4 | 4599 | 1 | 1 | 0 | 0.00 | LED OFF | 0 | cuvette dark
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

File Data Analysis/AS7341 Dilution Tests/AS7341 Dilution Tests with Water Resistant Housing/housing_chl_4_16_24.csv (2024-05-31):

Date and Time | ASTEP | ATIME | GAIN | LED Status | LED Intensity | Test | Seconds | Milliseconds | Type | F1 (Basic) | F2 (Basic) | F3 (Basic) | F4 (Basic) | F5 (Basic) | F6 (Basic) | F7 (Basic) | F8 (Basic) | Clear (Basic) | NIR (Basic) | Type | F1 (Raw) | F2 (Raw) | F3 (Raw) | F4 (Raw) | F5 (Raw) | F6 (Raw) | F7 (Raw) | F8 (Raw) | Clear (Raw) | NIR (Raw) | Approx Time
2112/5/32 (Thursday) 30:47:23 | 999 | 255 | 8 | LED ON | 255 | 0.0 | 3 | 3375 | BASIC COUNTS | 0.00 | 0.00 | 0.00 | 0.00 | 0.00 | 0.00 | 0.00 | 0.00 | 0.00 | 0.00 | RAW VALUES | 0 | 0 | 0 | 0 | 0 | 0 | 0 | 0 | 0 | 0 | time
2112/5/32 (Thursday) 30:47:26 | 999 | 255 | 8 | LED ON | 255 | 0.0 | 6 | 6413 | BASIC COUNTS | 0.00 | 0.01 | 0.00 | 0.00 | 0.00 | 0.00 | 0.00 | 0.00 | 0.01 | 0.00 | RAW VALUES | 295 | 465 | 38 | 18 | 11 | 17 | 17 | 10 | 601 | 0 | time
2112/5/32 (Thursday) 30:47:29 | 999 | 255 | 8 | LED ON | 255 | 0.0 | 9 | 9444 | BASIC COUNTS | 0.00 | 0.01 | 0.00 | 0.00 | 0.00 | 0.00 | 0.00 | 0.00 | 0.01 | 0.00 | RAW VALUES | 294 | 467 | 37 | 18 | 10 | 16 | 18 | 10 | 599 | 0 | time
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

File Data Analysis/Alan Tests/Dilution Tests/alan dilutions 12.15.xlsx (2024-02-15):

Date | Measurement Type | ug/L | Measurement Number | Measurement Value
12.15.23 | continuous | 50 | 1 | 83
12.15.23 | continuous | 50 | 2 | 81
12.15.23 | continuous | 50 | 3 | 81
12.15.23 | continuous | 50 | 4 | 81
12.15.23 | continuous | 50 | 5 | 84
12.15.23 | continuous | 50 | 6 | 79
12.15.23 | continuous | 50 | 7 | 79
12.15.23 | continuous | 50 | 8 | 81
12.15.23 | continuous | 50 | 9 | 83
12.15.23 | continuous | 50 | 10 | 92
12.15.23 | continuous | 50 | 11 | 78
12.15.23 | continuous | 50 | 12 | 79
12.15.23 | continuous | 50 | 13 | 84
12.15.23 | continuous | 50 | 14 | 83
12.15.23 | continuous | 50 | 15 | 87
12.15.23 | continuous | 50 | 16 | 83
12.15.23 | continuous | 50 | 17 | 79
12.15.23 | continuous | 50 | 18 | 78
12.15.23 | continuous | 50 | 19 | 85
12.15.23 | continuous | 50 | 20 | 75
12.15.23 | continuous | 50 | 21 | 82
12.15.23 | continuous | 50 | 22 | 84
12.15.23 | continuous | 50 | 23 | 79
12.15.23 | continuous | 50 | 24 | 86
12.15.23 | continuous | 50 | 25 | 84
12.15.23 | continuous | 50 | 26 | 84
12.15.23 | continuous | 50 | 27 | 80
12.15.23 | continuous | 50 | 28 | 83
12.15.23 | continuous | 50 | 29 | 82
12.15.23 | continuous | 50 | 30 | 86
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

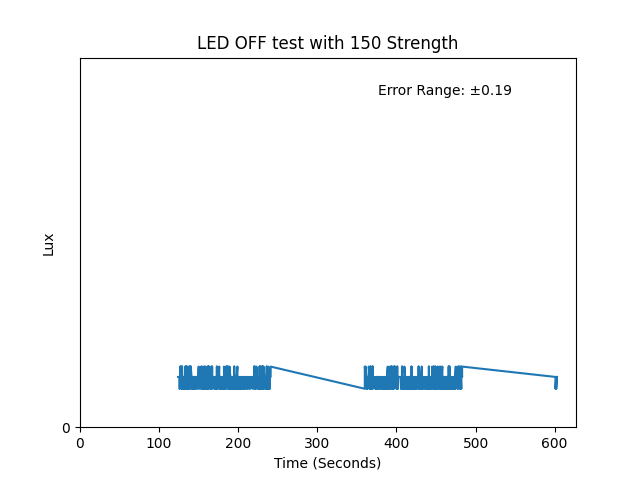
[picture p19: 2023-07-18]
LED_Tests/LED Intensity Change/LED_OFF_150_strength.png

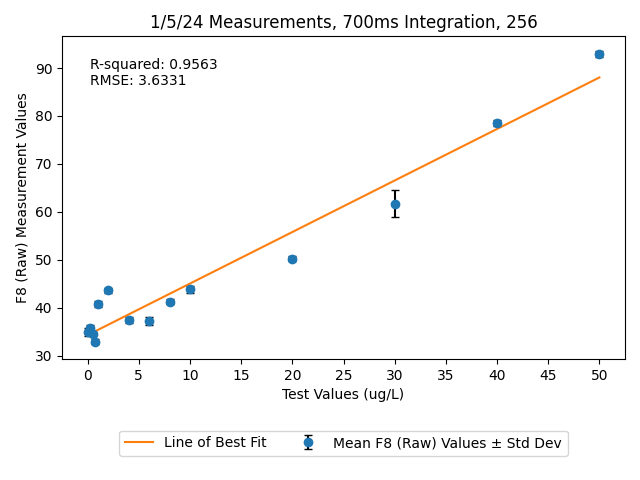
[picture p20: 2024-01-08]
Data Analysis/AS7341 Dilution Tests/AS7341 Dilutions 1.5.24/1_5_24_700ms_256x_graph.png

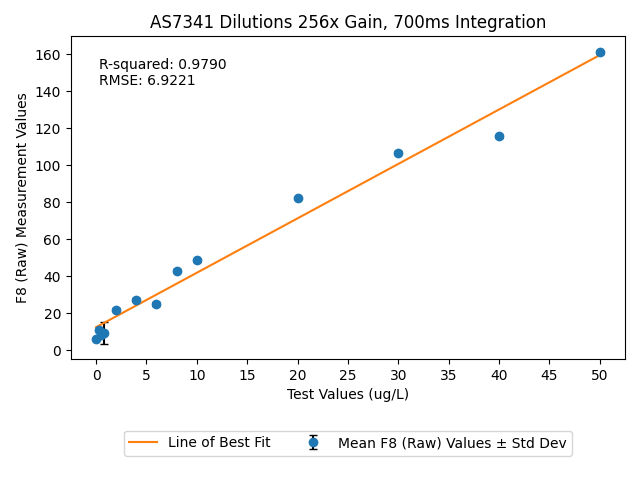
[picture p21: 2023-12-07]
Data Analysis/AS7341 Dilution Tests/AS7341 9.14.23/256x_700ms.png

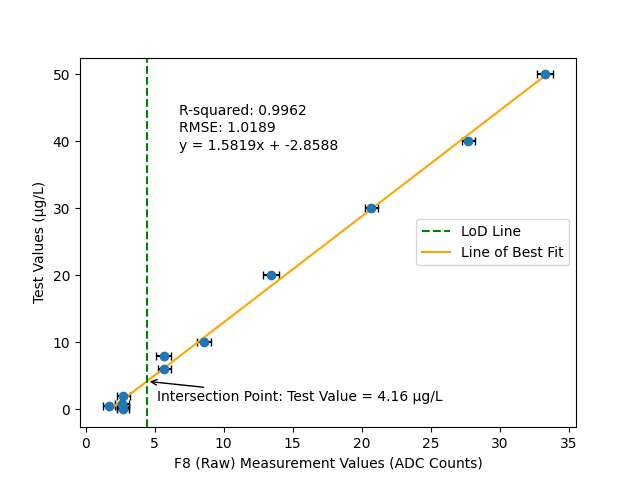
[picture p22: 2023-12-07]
Data Analysis/AS7341 Dilution Tests/AS7341_dillutions 8_22/256x_100ms_line_best_fit.png

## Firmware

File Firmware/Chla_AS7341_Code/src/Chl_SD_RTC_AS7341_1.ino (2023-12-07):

//This program monitors light while giving a time stamp and recording both
//basic counts and raw values to an SD card

#include <Adafruit_AS7341.h>
#include <Adafruit_AW9523.h>
#include "RTClibrary.h"
#include <SdFat.h>
#include <limits.h>
#include <numeric>

Adafruit_AS7341 as7341;
Adafruit_AW9523 aw;
RTC_PCF8523 rtc;
File myFile;
SdFat SD;

char daysOfTheWeek[7][12] = {"Sunday", "Monday", "Tuesday", "Wednesday", "Thursday", "Friday", "Saturday"};
const int SD_CHIP_SELECT = D5;
uint8_t LedPin = 0;
int LEDbright = 250;  // adjust this number as needed
int LEDdim = 1;       // adjust this number as needed

double calculateAverage(double sum, int count) {
    if (count == 0) {
        return 0.0; // or any other value to indicate an error or no data
    }
    return sum / static_cast<double>(count);
}

bool startLogging = false;

SYSTEM_THREAD(ENABLED);
SYSTEM_MODE(SEMI_AUTOMATIC);

void setup() {
  Serial.begin(9600);

  // Wait for communication with the host computer serial monitor
  while (!Serial) {
    delay(1);
  }
  
  if (!as7341.begin()){
    Serial.println("Could not find AS7341");
    while (1) { delay(10); }
  }
  
  // use ATIME of 103, ASTEP of 3457, and GAIN of 512x for dark counts during optical calibration
  as7341.setATIME(59);      
  as7341.setASTEP(599);
  as7341.setGain(AS7341_GAIN_4X);

  if (! rtc.begin()) {
    Serial.println("Couldn't find RTC");
    while (1);
  }

  if (! rtc.initialized()) {
    Serial.println("RTC is NOT running!");
    // following line sets the RTC to the date & time this sketch was compiled
    // rtc.adjust(DateTime(F(__DATE__), F(__TIME__)));
    // This line sets the RTC with an explicit date & time, for example to set
    // January 21, 2014 at 3am you would call:
    // rtc.adjust(DateTime(2014, 1, 21, 3, 0, 0));
  }

  if (! aw.begin(0x58)) {
    Serial.println("AW9523 not found? Check wiring!");
    while (1) delay(10);  // halt forever
  }

  Serial.println("AW9523 found!");
  aw.pinMode(LedPin, AW9523_LED_MODE);

  SD.begin(SD_CHIP_SELECT);
 
  File file = SD.open("data.csv", FILE_WRITE);

  if (file) {
    file.print("ASTEP:");
    file.print(',');
    file.println(as7341.getASTEP());
    file.print("ATIME:");
    file.print(',');
    file.println(as7341.getATIME());
    file.print("GAIN (check table):");
    file.print(',');
    file.println(as7341.getGain());
    // 0.5x records as 0, 1x records as 1, 2x records as 2, 4x records as 3, 
    // 8x records as 4, 16x records as 5, 32x records as 6, 64x records as 7,
    // 128x records as 8, 256x records as 9, 512x records as 10.
    file.println(" ");
    file.println("LED Intensity,Date,Time,Type,F1 (Basic),F2 (Basic),F3 (Basic),F4 (Basic),F5 (Basic),F6 (Basic),F7 (Basic),F8 (Basic),Clear (Basic),NIR (Basic),Type,F1 (Raw),F2 (Raw),F3 (Raw),F4 (Raw),F5 (Raw),F6 (Raw),F7 (Raw),F8 (Raw),Clear (Raw),NIR (Raw)"); // Headers
    file.close();
  } else {
    Serial.println(F("Error opening file!"));
  }
}

void loop() {


  // put your main code here, to run repeatedly:

  //File file = SD.open("data.csv", FILE_WRITE);
  //DateTime now = rtc.now();

  // Switch LED intensity to bright.

  unsigned long currentTime = millis();  // Current time in milliseconds
  unsigned long onTime = 500;  // 1 second on time
  unsigned long offTime = 500;  // 1 second off time

  // Calculate the time elapsed since the start of the loop
  unsigned long elapsedTime = currentTime % (onTime + offTime);



  bool isLedOn = (elapsedTime < onTime);
  aw.analogWrite(LedPin, isLedOn ? LEDbright : LEDdim); // Turn LED on or off
  // aw.analogWrite(LedPin, 250);

  //delay(100);

  serialprintresults();
  
  //save data to SD card

  // if (file) {

    //  print readings
     
    // file.print("LED BRIGHT");
  
    
    fileprintresults();
  // }

  // else {
  //  Serial.println(F("Error opening file!"));
  //}

  //delay(250);

//  Switch LED intensity to dim.



  bool isLedOff = (elapsedTime < offTime);
  aw.analogWrite(LedPin, isLedOff ? LEDdim : LEDbright);
  // aw.analogWrite(LedPin, 1);

  //delay(100);

  serialprintresults();
  
  //save data to SD card
  
  //if (file) {

    //  print readings
     
    //file.print("LED DIM");

  fileprintresults();



//else {
  //  Serial.println(F("Error opening file!"));
 // }

 // delay(250);

}

void serialprintresults() 
{

DateTime now = rtc.now();
unsigned long decimalseconds_to_record = (millis() % 1000)/1; //the divided by 1 has to stay, otherwise the program gets stuck during serial monitor!

Serial.print("LED INTENSITY:");
  Serial.print(" ");
  Serial.println(LEDbright);
  Serial.println();
  Serial.print(now.year(), DEC);
  Serial.print('/');
  Serial.print(now.month(), DEC);
  Serial.print('/');
  Serial.print(now.day(), DEC);
  Serial.print(" (");
  Serial.print(daysOfTheWeek[now.dayOfTheWeek()]);
  Serial.print(") ");
  Serial.print(now.hour(), DEC);
  Serial.print(':');
  Serial.print(now.minute(), DEC);
  Serial.print(':');
  Serial.print(now.second(), DEC);
  Serial.print('.');
  Serial.print(decimalseconds_to_record, DEC);
  Serial.println();

  uint16_t readings[12];
  float counts[12];

    if (!as7341.readAllChannels(readings)){
    Serial.println("Error reading all channels!");
    return;
  }

  for(uint8_t i = 0; i < 12; i++) {
    if(i == 4 || i == 5) continue;
    // we skip the first set of duplicate clear/NIR readings
    // (indices 4 and 5)
    counts[i] = as7341.toBasicCounts(readings[i]);
  }

  Serial.print("F1 415nm : ");
  Serial.print(counts[0]);
  Serial.print("  ");
  Serial.print("Raw Value : ");
  Serial.println(readings[0]);
  Serial.print("F2 445nm : ");
  Serial.print(counts[1]);
  Serial.print("  ");
  Serial.print("Raw Value : ");
  Serial.println(readings[1]);
  Serial.print("F3 480nm : ");
  Serial.print(counts[2]);
  Serial.print("  ");
  Serial.print("Raw Value : ");
  Serial.println(readings[2]);
  Serial.print("F4 515nm : ");
  Serial.print(counts[3]);
  Serial.print("  ");
  Serial.print("Raw Value : ");
  Serial.println(readings[3]);
  Serial.print("F5 555nm : ");

  // again, we skip the duplicates  

  Serial.print(counts[6]);
  Serial.print("  ");
  Serial.print("Raw Value : ");
  Serial.println(readings[6]);
  Serial.print("F6 590nm : ");
  Serial.print(counts[7]);
  Serial.print("  ");
  Serial.print("Raw Value : ");
  Serial.println(readings[7]);
  Serial.print("F7 630nm : ");
  Serial.print(counts[8]);
  Serial.print("  ");
  Serial.print("Raw Value : ");
  Serial.println(readings[8]);
  Serial.print("F8 680nm : ");
  Serial.print(counts[9]);
  Serial.print("  ");
  Serial.print("Raw Value : ");
  Serial.println(readings[9]);
  Serial.print("Clear    : ");
  Serial.print(counts[10]);
  Serial.print("  ");
  Serial.print("Raw Value : ");
  Serial.println(readings[10]);
  Serial.print("NIR      : ");
  Serial.print(counts[11]);
  Serial.print("  ");
  Serial.print("Raw Value : ");
  Serial.println(readings[11]);
  Serial.print("  ");
  Serial.println();
}

void fileprintresults() 
{

File file = SD.open("data.csv", FILE_WRITE);
DateTime now = rtc.now();
unsigned long decimalseconds_to_record = (millis() % 1000)/1; //the divided by 1 has to stay, otherwise the program gets stuck during serial monitor!

 uint16_t readings[12];
  float counts[12];

    if (!as7341.readAllChannels(readings)){
    Serial.println("Error reading all channels!");
    return;
  }

  for(uint8_t i = 0; i < 12; i++) {
    if(i == 4 || i == 5) continue;
    // we skip the first set of duplicate clear/NIR readings
    // (indices 4 and 5)
    counts[i] = as7341.toBasicCounts(readings[i]);
  }

if (file) {

  unsigned long currentTime = millis();  // Current time in milliseconds
  unsigned long onTime = 500;  // 1 second on time
  unsigned long offTime = 500;  // 1 second off time

  // Calculate the time elapsed since the start of the loop
  unsigned long elapsedTime = currentTime % (onTime + offTime);

  bool isLedOn = (elapsedTime < onTime);

  //delay(100);

  file.print(isLedOn ? LEDbright : LEDdim);
    file.print(',');
file.print(now.year(), DEC);
    file.print('/');
    file.print(now.month(), DEC);
    file.print('/');
    file.print(now.day(), DEC);
    file.print(" (");
    file.print(daysOfTheWeek[now.dayOfTheWeek()]);
    file.print(") ");
    file.print(',');
    file.print(now.hour(), DEC);
    file.print(':');
    file.print(now.minute(), DEC);
    file.print(':');
    file.print(now.second(), DEC);
    file.print(':');
    file.print(decimalseconds_to_record, DEC);
    file.print(',');
    file.print("BASIC COUNTS");
    file.print(',');
    file.print(counts[0]);
    file.print(',');
    file.print(counts[1]);
    file.print(',');
    file.print(counts[2]);
    file.print(',');
    file.print(counts[3]);
    file.print(',');
    file.print(counts[6]);
    file.print(',');
    file.print(counts[7]);
    file.print(',');
    file.print(counts[8]);
    file.print(',');
    file.print(counts[9]);
    file.print(',');
    file.print(counts[10]);
    file.print(',');
    file.print(counts[11]);
    file.print(',');
    file.print("RAW VALUES");
    file.print(',');
    file.print(readings[0]);
    file.print(',');
    file.print(readings[1]);
    file.print(',');
    file.print(readings[2]);
    file.print(',');
    file.print(readings[3]);
    file.print(',');
    file.print(readings[6]);
    file.print(',');
    file.print(readings[7]);
    file.print(',');
    file.print(readings[8]);
    file.print(',');
    file.print(readings[9]);
    file.print(',');
    file.print(readings[10]);
    file.print(',');
    file.println(readings[11]);
    file.close();

}

else {
    Serial.println(F("Error opening file!"));
  }

}

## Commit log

2023-06-20 Code/ Code containing LED circuit driver
2023-06-20 Create Code with LED Circuit Driver
2023-06-20 Circuit Diagram with LED circuit driver
2023-06-28 Update and rename Code with LED Circuit Driver to Code
2023-06-28 Create Circuit Diagram
2023-07-07 Create LED_Lux_Values
2023-07-07 Create graph lux data when LED is on
2023-07-07 Create graph lux data when LED is off
2023-08-07 Create Sample Measurements Filter Test
2023-08-21 tweak notebook to use stdev in plots and print out more info
2023-08-23 Create Sample Dilutions AS7341 8_22_23
2024-01-09 Create Cuvette Holder New Optics
2024-03-04 Create LED with Marine Expoxy
